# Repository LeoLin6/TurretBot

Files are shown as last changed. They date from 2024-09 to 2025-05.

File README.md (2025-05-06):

# TurretBot for automated acoustic experiments. 

Already have the hardware setup? Jump to the [Software section](#Software).

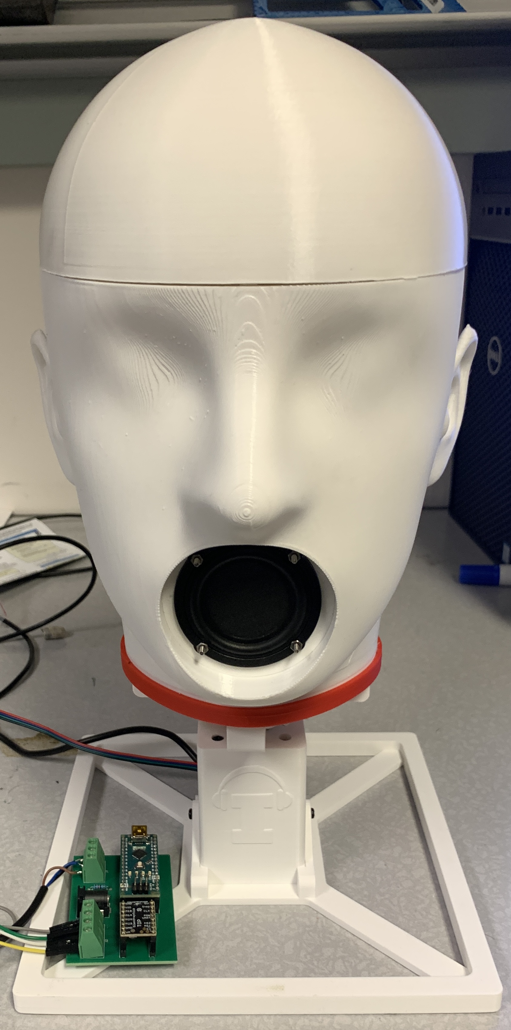
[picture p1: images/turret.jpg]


## Sourcing the parts

#### 🧾 Fabrication Files

All files required for manufacturing the PCB can be found here:  
👉 [PCB Manufacturing Files](./tmc%20pcb%20manufacturing%20files/feb2025_fab)

#### 🔩 Component List

| Part Name                                                | Quantity | Designation on Schematic         | Link                                                                 |
|----------------------------------------------------------|----------|----------------------------------|----------------------------------------------------------------------|
| Barrel Jack for power                                    | 1        | J1 (Barrel_Jack)                 | [digikey](https://www.digikey.com/en/products/detail/same-sky-formerly-cui-devices/PJ-002A/96962)           |
| PinSocket headers for Arduino Nano                       | 2        | J3, J5                            | [digikey](https://www.digikey.com/en/products/detail/sullins-connector-solutions/PPTC151LFBN-RC/810153)     |
| PinSocket headers for TMC 2208 driver chip               | 2        | J4, J6                            | [digikey](https://www.digikey.com/en/products/detail/w%C3%BCrth-elektronik/61300811821/17737805)            |
| Induction sensor terminal block                          | 1        | J7                                | [digikey](https://www.digikey.com/en/products/detail/phoenix-contact/1715734/260632)                        |
| Terminal Block for stepper motor                         | 1        | J2 (Screw_Terminal for motor)     | [digikey](https://www.digikey.com/en/products/detail/phoenix-contact/1715747/260633)                        |
|TMC 2208 motor driver chip                                 | 1        |  None                            | [digikey](https://www.digikey.com/short/j84mhvfm)|
| Adafruit adjustable power supply  (Run it at 18 Volts)            | 1         | None                                | [digikey](https://www.digikey.com/short/31r0mw15)  |
| Induction sensor                                      | 1         | None                                  | [amazon](https://www.amazon.com/Taiss-NO%EF%BC%88Normally-LJ12A3-4-Z-inductive-Proximity/dp/B073XD44CW) |

## 🔧 Assembly Instructions

Follow the designators on this PCB to solder the parts above: ([also have schematic for reference](./images/pcb_v2_schematic.png))

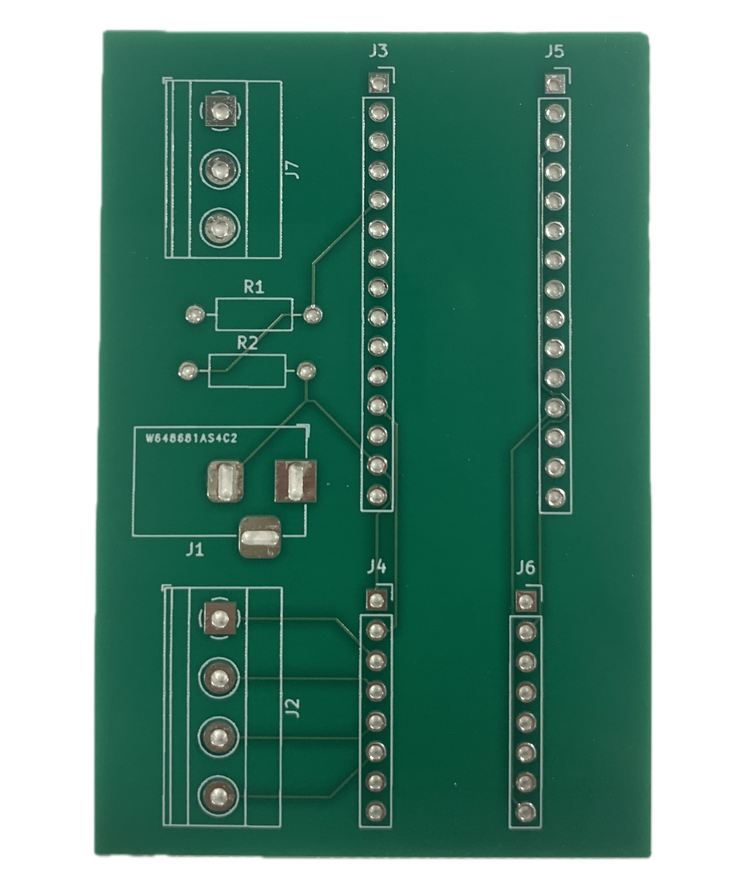
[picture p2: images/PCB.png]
PCB


Final assembled PCB:

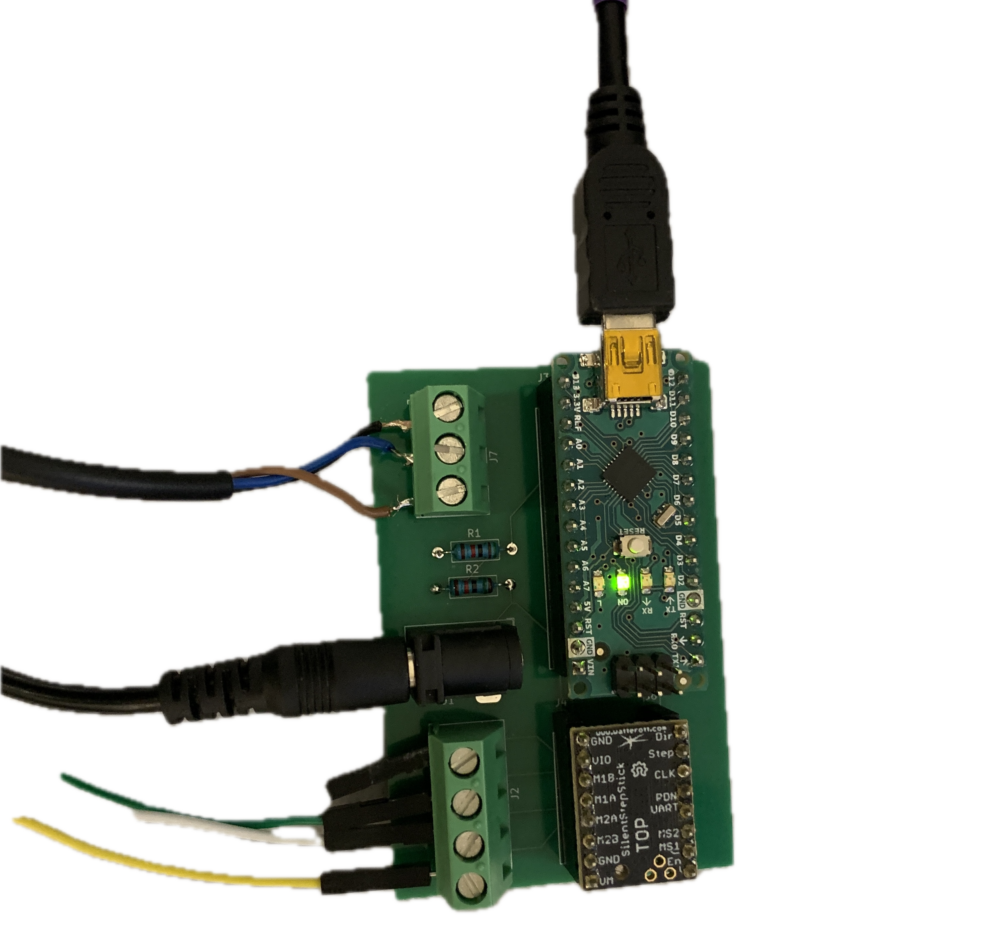
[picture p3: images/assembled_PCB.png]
Final Assembled PCB


For motor connector reference (What's color code M1B, M1A etc)
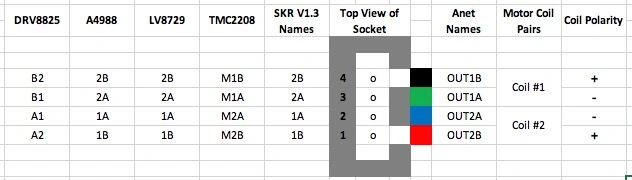
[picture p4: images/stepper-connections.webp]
color code Image


Follow this github tutorial to Solder UART bridge on tmc 2208 chip:
https://github.com/teemuatlut/TMC2208Stepper?tab=readme-ov-file

## Software

### 1. Clone the Repository
```bash
git clone https://github.com/LeoLin6/TurretBot.git
cd TurretBot
```

### 2. Install Arduino IDE

If you don't already have the Arduino IDE installed, download and install it from the official website:  
🔗 [https://www.arduino.cc/en/software](https://www.arduino.cc/en/software)

### 3. Flash the Arduino

1. **Open Arduino IDE**  
2. **Go to:**  
   `File` → `Open` → Navigate to `TurretBot/main/src/experiment_arduino/experiment_arduino.ino`
3. **Connect your Arduino** via USB to your PC.
4. **Select the correct board and port**:  
   - `Tools` → `Board` → Select the correct Arduino board (e.g., Arduino Uno)  
   - `Tools` → `Port` → Select the appropriate COM port (note it down, you'll need it for the next step)  
5. **Click Upload** (the right-arrow icon) to flash the firmware to the Arduino.

### 4. Run the Python Script for Calibration

1. Make sure you have Python installed (preferably Python 3.x).  
2. Navigate to the script directory:
```bash
cd main/src
```
3. Run the script:
```bash
python experiment.py
```
4. Follow the terminal prompts for calibration and testing positional movement.

> 💡 Make sure the COM port in the script matches the one your Arduino is using.

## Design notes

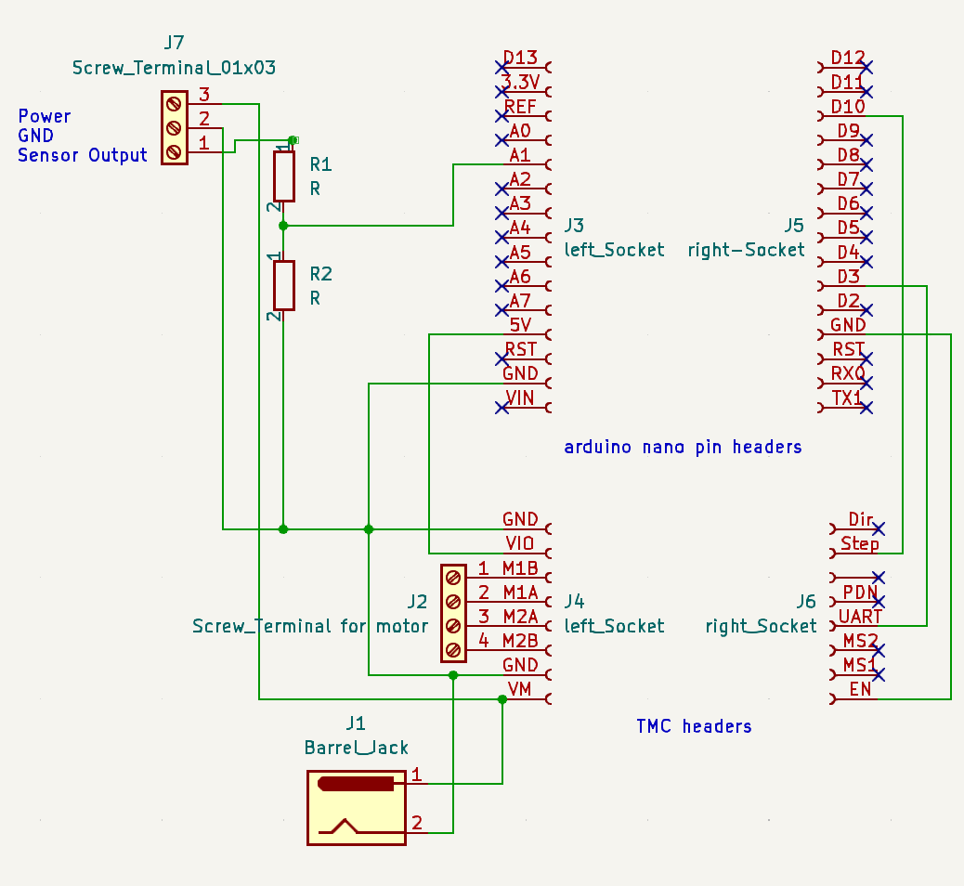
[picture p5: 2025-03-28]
images/pcb_v2_schematic.png

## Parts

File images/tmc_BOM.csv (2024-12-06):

Id | Designator | Footprint | Quantity | Designation | Supplier and ref
1 | J1 | BarrelJack_Horizontal | 1 | Barrel_Jack
2 | J3 | PinSocket_1x15_P2.54mm_Vertical | 1 | left_Socket
3 | J6 | PinSocket_1x08_P2.54mm_Vertical | 1 | right_Socket
4 | J5 | PinSocket_1x15_P2.54mm_Vertical | 1 | right-Socket
5 | J2 | TerminalBlock_Phoenix_MKDS-1,5-4_1x04_P5.00mm_Horizontal | 1 | Screw_Terminal for motor
6 | J4 | PinSocket_1x08_P2.54mm_Vertical | 1 | left_Socket

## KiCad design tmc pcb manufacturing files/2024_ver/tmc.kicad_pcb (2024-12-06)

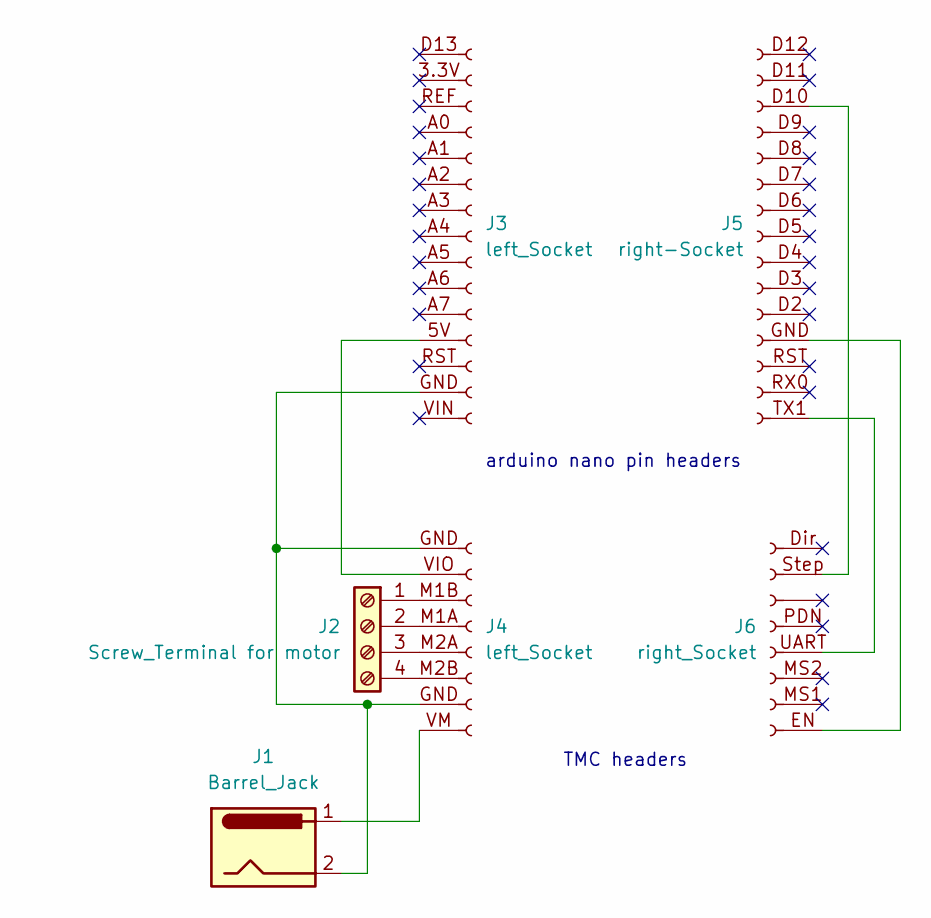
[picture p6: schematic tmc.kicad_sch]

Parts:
J1: Barrel_Jack; BarrelJack_Horizontal
J2: Screw_Terminal for motor; TerminalBlock_Phoenix_MKDS-1,5-4_1x04_P5.00mm_Horizontal
J3: left_Socket; PinSocket_1x15_P2.54mm_Vertical
J4: left_Socket; PinSocket_1x08_P2.54mm_Vertical
J5: right-Socket; PinSocket_1x15_P2.54mm_Vertical
J6: right_Socket; PinSocket_1x08_P2.54mm_Vertical

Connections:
unnamed: J2.1, J4.M1B (Pin_3)
unnamed: J2.2, J4.M1A (Pin_4)
unnamed: J2.3, J4.M2A (Pin_5)
unnamed: J2.4, J4.M2B (Pin_6)
unnamed: J3.5V (Pin_12), J4.VIO (Pin_2)
unnamed: J1.2, J3.GND (Pin_14), J4.GND (Pin_1)
unnamed: J1.1, J4.VM (Pin_8)
unnamed: J5.D10 (Pin_3), J6.Step (Pin_2)
unnamed: J5.GND (Pin_12), J6.EN (Pin_8)
unnamed: J5.TX1 (Pin_15), J6.UART (Pin_5)

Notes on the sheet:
TMC headers
arduino nano pin headers

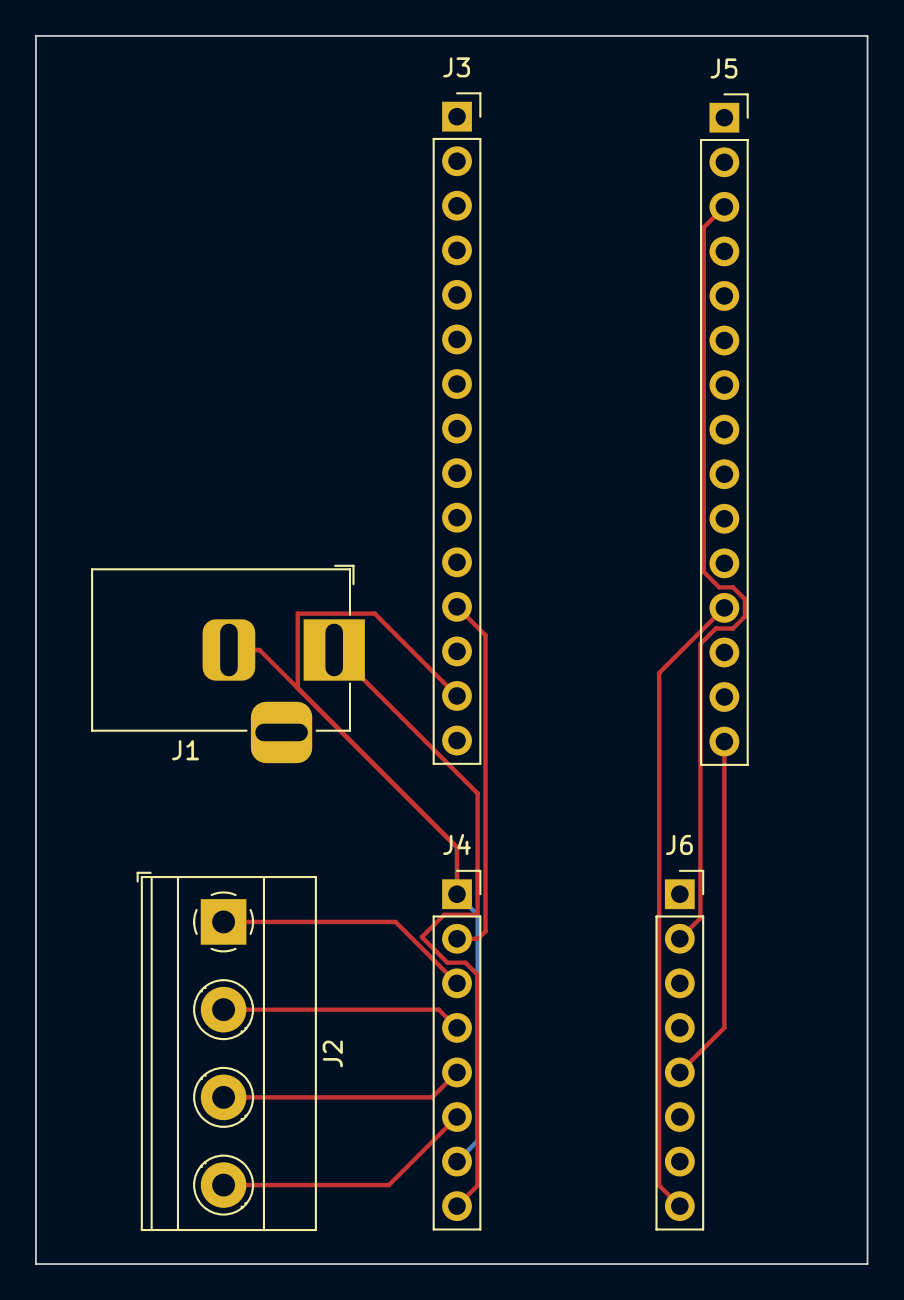
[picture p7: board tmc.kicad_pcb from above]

Board: 2 copper layers, 47.4 x 70.0 mm, 6 parts (0 on the bottom side), 10 nets.

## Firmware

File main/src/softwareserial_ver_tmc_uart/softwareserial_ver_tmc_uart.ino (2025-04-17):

// Defining
//using software serial to control tmc 2208 chip through UART
int x;
#define StepPin     10
#define RX_PIN      2
#define TX_PIN      3
#define EN          12
#define Pin         A1 //for induction sensor



#define Current     726
#define MicroStep   0     // 0: Native 256 microstep setting.
                          // 1: 128 microsteps per full step.
                          // 2: 64 microsteps per full step.
                          // 3: 32 microsteps per full step.
                          // 4: 16 microsteps per full step.
                          // 5: 8 microsteps per full step.
                          // 6: 4 microsteps per full step.
                          // 7: 2 microsteps per full step.
                          // 8: Full step.

const int microsteps = 64;                
const double stepAngle = 360.0 / (200.0 * microsteps); 
const int pulseWidth = 200; // microseconds


// Including library
#include <TMC2208Stepper.h>                                // Include library
#include <SoftwareSerial.h> 

SoftwareSerial mySerial(RX_PIN, TX_PIN);
TMC2208Stepper driver = TMC2208Stepper(&mySerial);    // Create driver and use

// Setup
void setup() {
  //driver.beginSerial(115200); 
  mySerial.begin(115200);  
  driver.push();
  Serial.begin(115200);

  // Prepare pins
  pinMode(StepPin, OUTPUT);
  pinMode(EN, OUTPUT);

  driver.pdn_disable(1);              // Use PDN/UART pin for communication
  driver.I_scale_analog(0);           // Adjust current from the registers
  driver.rms_current(Current);        // Set driver current 
  driver.toff(5);                     // Enable driver
  //digitalWrite(EN, LOW);
  
  driver.en_spreadCycle(0);           // 1: spreadCycle
                                      // 0: stealthChop
  driver.pwm_autoscale(1);            // 1: if stealthChop is chosen. Otherwise 0
  driver.mstep_reg_select(1);
  //driver.mres(MicroStep); 
  //run_calibration_seq();
  driver.microsteps(microsteps);
  //delay(1000);
  //run_rps_for_duration(0.05, 10);
/*
  AccelToSpeed(1.0);
  run_rps(1.0);
  delay(10000);
  DecelFromSpeed(1);
*/}

void MoveToPosition(double degrees){
  bool backwards = 0;
  if(degrees<0){
    degrees = degrees * -1;
    driver.shaft(1);
    //delayMicroseconds(100);
    backwards = 1;
  }
  long steps = degrees/stepAngle; // Convert degrees to steps
  
  for (long i = 0; i < steps; i++) {
    //Serial.print(steps);
    digitalWrite(StepPin, HIGH); // Create a step pulse
    delayMicroseconds(pulseWidth); // Pulse width
    digitalWrite(StepPin, LOW); // End pulse
    delayMicroseconds(pulseWidth); // Delay between steps
  }
  if(backwards)
    driver.shaft(0); // switch back to normal direction

}

//runs motor at desired rps
void run_rps(double rps){
  driver.VACTUAL(rps / 0.715 * 256 * 200);
}
/*
void run_rps_for_duration(double rps, double duration) {
  driver.shaft(0);
  const int steps_per_rev = 200;
  const int microsteps = 2;
  const int pulseWidth = 100; // in microseconds — safe default

  // Total microsteps per revolution
  const int microsteps_per_rev = steps_per_rev * microsteps;

  // Time between steps
  double usec_per_step = 1000000.0f / (float(microsteps_per_rev));

  // Total number of steps to run
  unsigned long total_steps = rps * duration * microsteps_per_rev;

  for (unsigned long i = 0; i < total_steps; i++) {
    digitalWrite(StepPin, HIGH);
    delayMicroseconds(pulseWidth);
    digitalWrite(StepPin, LOW);
    delayMicroseconds(usec_per_step/rps - pulseWidth);
  }
  delay(1000);
}*/

void run_rps_for_duration(double rps, double duration) {
  //driver.shaft(0); // Set direction

  const int steps_per_rev = 200;
  
  

  const int microsteps_per_rev = steps_per_rev * microsteps;
  const double usec_per_step = 1000000.0f / (rps * microsteps_per_rev);
  const unsigned long total_steps = rps * duration * microsteps_per_rev;

  unsigned long start_time = micros();
  double next_step_time = start_time;

  for (unsigned long i = 0; i < total_steps; i++) {
    // Wait until it's time for the next step
    while ((double)micros() < next_step_time);

    digitalWrite(StepPin, HIGH);
    delayMicroseconds(pulseWidth);
    digitalWrite(StepPin, LOW);

    next_step_time += usec_per_step;
  }

  // Optional pause
  delay(1000);
}

/*

void run_rps_for_duration (double rps, double time){
  run_rps(rps);
  delay(time*1000);
  run_rps(0);
}*/

//takes rps as input, accelerates to rps speed from 0rps in 1.0seconds. 
void AccelToSpeed(double rps){
  for(double i=0; i<rps; i+= rps/100){
    run_rps(i);
    delay(10);
  }
}

//takes rps as input decelerates to 0 from that rps value in 1.0seconds. 
void DecelFromSpeed(double rps){
  for(double i=rps; i>=0; i-= rps/100){
    run_rps(i);
    delay(10);
  }
}
// Looping
float duration;
void loop() {
  if (Serial.available()){
    String str = Serial.readStringUntil('\n');
    str.trim();
     

    if(str=="cali"){               //home in seq if input is a 1
    x = Serial.readStringUntil('\n').toFloat();
      run_calibration_seq(x);
    }else if (str == "pos"){
      //x = Serial.readString().toFloat(); 
      x = Serial.readStringUntil('\n').toFloat();
      MoveToPosition(x);
    } else if (str == "vel"){
      x = Serial.readStringUntil('\n').toFloat();
      duration = Serial.readStringUntil('\n').toFloat(); 
      run_rps_for_duration(x/100.0, 10);
      //run_rps_for_duration(x, duration);
    }
    
    
    Serial.print(x); 
  }
}

void run_calibration_seq(double del){
    while(digitalRead(Pin)!=HIGH){
      run_rps(0.05);
      //Serial.println("no object");
    }
    delay(del);
    //Serial.println("Object detected");
    run_rps(0);
    delay (100);
}

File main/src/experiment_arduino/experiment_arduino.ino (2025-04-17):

// -----------------------------
// Pin Definitions
// -----------------------------
#define STEP_PIN    10
#define RX_PIN      2
#define TX_PIN      3
#define EN_PIN      12
#define SENSOR_PIN  A1 // Inductive sensor

// -----------------------------
// Configuration Constants
// -----------------------------
#define CURRENT       726
#define MICROSTEP     0  // Used for driver.mres() if needed
const int microsteps = 64;
const double stepAngle = 360.0 / (200.0 * microsteps); // degrees per microstep
const int pulseWidth = 200; // microseconds

// -----------------------------
// Library Includes
// -----------------------------
#include <TMC2208Stepper.h>
#include <SoftwareSerial.h>

// -----------------------------
// Global Objects and Variables
// -----------------------------
SoftwareSerial mySerial(RX_PIN, TX_PIN);
TMC2208Stepper driver = TMC2208Stepper(&mySerial);
float duration;
float x;

// -----------------------------
// Setup Function
// -----------------------------
void setup() {
  Serial.begin(115200);
  mySerial.begin(115200);

  pinMode(STEP_PIN, OUTPUT);
  pinMode(EN_PIN, OUTPUT);
  pinMode(SENSOR_PIN, INPUT);

  driver.pdn_disable(1);                // Use UART communication
  driver.I_scale_analog(0);             // Use digital current control
  driver.rms_current(CURRENT);          // Set current
  driver.toff(5);                        // Enable driver (low time)
  driver.en_spreadCycle(0);             // Use stealthChop mode
  driver.pwm_autoscale(1);              // Enable voltage regulator
  driver.mstep_reg_select(1);
  driver.microsteps(microsteps);        // Set microstep resolution

  driver.push(); // Apply settings
}

// -----------------------------
// Loop Function
// -----------------------------
void loop() {
  if (Serial.available()) {
    String cmd = Serial.readStringUntil('\n');
    cmd.trim();

    if (cmd == "cali") {
      x = Serial.readStringUntil('\n').toFloat();
      run_calibration_seq(x);

    } else if (cmd == "pos") {
      x = Serial.readStringUntil('\n').toFloat();
      MoveToPosition(x);

    } else if (cmd == "vel") {
      float rps = Serial.readStringUntil('\n').toFloat() / 100.0;
      float dur = Serial.readStringUntil('\n').toFloat() / 100.0;
      run_rps_for_duration(rps, dur);
    }

    Serial.println(x); // Echo value
  }
}

// -----------------------------
// Motion & Control Functions
// -----------------------------

// Move a specific number of degrees
void MoveToPosition(double degrees) {
  bool backwards = false;
  
  if (degrees < 0) {
    degrees *= -1;
    driver.shaft(1);  // Reverse direction
    backwards = true;
  }

  long steps = degrees / stepAngle;
  for (long i = 0; i < steps; i++) {
    digitalWrite(STEP_PIN, HIGH);
    delayMicroseconds(pulseWidth);
    digitalWrite(STEP_PIN, LOW);
    delayMicroseconds(pulseWidth+1000);
  }

  if (backwards) driver.shaft(0); // Restore direction
}

// Run motor at a constant RPS
void run_rps(double rps) {
  driver.VACTUAL(rps / 0.715 * 256 * 200); // Empirical conversion
}

// Run motor for specific duration at RPS
void run_rps_for_duration(double rps, double duration) {
  const int stepsPerRev = 200;
  const int microstepsPerRev = stepsPerRev * microsteps;
  const double usecPerStep = 1000000.0 / (rps * microstepsPerRev);
  const unsigned long totalSteps = rps * duration * microstepsPerRev;

  unsigned long start_time = micros();
  double nextStepTime = start_time;

  for (unsigned long i = 0; i < totalSteps; i++) {
    while ((double)micros() < nextStepTime);
    
    digitalWrite(STEP_PIN, HIGH);
    delayMicroseconds(pulseWidth);
    digitalWrite(STEP_PIN, LOW);

    nextStepTime += usecPerStep;
  }

  delay(1000); // Optional delay
}

// Accelerate to a target RPS in ~1s
void AccelToSpeed(double rps) {
  for (double i = 0; i <= rps; i += rps / 100) {
    run_rps(i);
    delay(10);
  }
}

// Decelerate from current RPS to 0 in ~1s
void DecelFromSpeed(double rps) {
  for (double i = rps; i >= 0; i -= rps / 100) {
    run_rps(i);
    delay(10);
  }
}

// Run calibration sequence until sensor is triggered
void run_calibration_seq(double delayTime) {
  while (digitalRead(SENSOR_PIN) != HIGH) {
    run_rps(0.05);
  }

  delay(delayTime);
  run_rps(0);
  delay(100);
}

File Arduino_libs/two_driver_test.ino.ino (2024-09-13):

#include <AccelStepper.h>
#include <MultiStepper.h>
#include <Servo.h>

/* README: procedure:
For some specified payload motor speed (this is what is being measured acoustically):
1. Initialize ang=0. Move to ang
2. Run payload motor at speed S for T seconds
3. ang += ang_step
4. Repeat

Run the above for various speeds S as specified below

AUDIO CUES:
1 chirp: end of one azimuth step
2 chirps: end of calibration sequence (homing procedure)
3 chirps: end of one full revolution in azimuth
*/

#define HOMING_PIN 8 //for induction sensor
#define ALARM_PIN 6 // for whatever sound-making sensor is
#define TEST_SERVO_PIN 9
#define PAUSE_CHIRP 500 // ms
#define PAUSE_SHORT 200 // ms
#define PAUSE_LONG 30000 // ms
#define PAUSE_MEASURE 10000 // ms, how long to run the test motor per pose
#define PAUSE_NOISEONLY 10000 // ms

#define TABLE_MAXSPEED 2000 // steps per sec
#define TABLE_SPEED 500 // steps per sec
#define TABLE_STEPS_PER_REV 6400
#define TABLE_NUM_ANGLES 24 // corresponds to a resolution of 15 deg.

#define TEST_MAX_SPEED 2000
#define TEST_STEPS_PER_REV 6400
#define TEST_MINSPR 2 // fastest (SPR = seconds per Revolution)
#define TEST_INCSPR 2 // so for each `experiment` call, increment speed `secperrev` by this much
#define TEST_NUM_SPR 5

// GLOBAL VARS
// Define the stepper motor and the HOMING_PINs that is connected to
AccelStepper tableMotor(1, 2, 5); //turntable motor
AccelStepper testMotor(1, 3, 4); //experiement motor
Servo testServo;
Servo alarm;

void setup() {
  // turntable setup
  tableMotor.setMaxSpeed(TABLE_MAXSPEED);
  tableMotor.setSpeed(TABLE_SPEED); // Set maximum speed value for the stepper

  // alarm setup
  alarm.attach(ALARM_PIN);
  alarm.write(0); //reset servo to position 0
 
  // run away!!!!
  delay(PAUSE_LONG);
  doAlarmChirp(4);
  delay(PAUSE_NOISEONLY);
  doAlarmChirp(4);
}

void loop() {
  for (int n=0; n<TEST_NUM_SPR; n++) {
    int secs_per_rev = TEST_MINSPR + n * TEST_INCSPR;
    experiment(secs_per_rev);
  }
}

void experiment(int secs_per_rev){
  // test motor setup
  testMotor.setMaxSpeed(TEST_STEPS_PER_REV);
  testMotor.setSpeed(TEST_STEPS_PER_REV / secs_per_rev);
  
  // reset turntable
  TableToHome();
  tableMotor.setCurrentPosition(0);
  tableMotor.setSpeed(TABLE_SPEED);
  doAlarmChirp(2);

  for (int step=0; step<TABLE_NUM_ANGLES; step ++) {

    // do one discrete step
    int tableStep1 = int(TABLE_STEPS_PER_REV/TABLE_NUM_ANGLES*step);
    while(tableMotor.currentPosition()<=tableStep1){ tableMotor.runSpeed(); }
    delay(PAUSE_SHORT);

    doAlarmChirp(1);
    delay(PAUSE_SHORT);

    //play test motor for 10 seconds
    unsigned long t1 = millis()+PAUSE_MEASURE;
    testServo.attach(TEST_SERVO_PIN);
    testServo.write(180);
    while(millis() < t1){ 
      testMotor.runSpeed();
    }
    testServo.detach();
    delay(PAUSE_SHORT);

    }
  // CABLE MANAGEMENT
  doAlarmChirp(3);

  tableMotor.setSpeed(-TABLE_SPEED);
  while(tableMotor.currentPosition()>-100){
    tableMotor.runSpeed();
  }
  tableMotor.setSpeed(TABLE_SPEED);
}

void TableToHome(){
    while(digitalRead(HOMING_PIN)!=HIGH){
      tableMotor.runSpeed();
      Serial.println("no object");
    }
    // tableMotor.stop();
    tableMotor.setCurrentPosition(0);
    tableMotor.setSpeed(TABLE_SPEED);
    // tableMotor.runToNewPosition(100);

    Serial.println("Object detected");
    //delay(1000);
    
}

void doAlarmChirp(int num){
  for (int i = 0; i < num; i++) {
    delay(PAUSE_SHORT);
    alarm.write(180);
    delay(PAUSE_SHORT);
    alarm.write(0);
    delay(PAUSE_SHORT);
  }
  delay(PAUSE_CHIRP);  
}

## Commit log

2024-02-21 Create turret_control_accel.ino
    How to use accel stepper library to control a turret w/ two stepper motors.
2024-09-13 Add files via upload
    Last year's more polished files for the final acoustic tests of turrets in different configurations. Also motor testing with diff drivers
2025-02-03 updated
    yeah
    [tmc-B_Cu.gbr, tmc-B_Mask.gbr, tmc-B_Paste.gbr, tmc-B_Silkscreen.gbr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]
2025-02-07 new project for semester: turntable on pcb
2025-02-21 ver_2_fab_files
    uploaded fabrication files for pcb version 2
    [tmc-B_Cu.gbr, tmc-B_Mask.gbr, tmc-B_Paste.gbr, tmc-B_Silkscreen.gbr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]
2025-02-21 changed BOM
    [tmc.xlsx]
2025-03-28 Updated schematic with induction sensor wirings
2025-04-17 new commit
    [tmc_BOM.csv, tmc_oct_14.kicad_pcb, tmc_oct_14.kicad_sch]
